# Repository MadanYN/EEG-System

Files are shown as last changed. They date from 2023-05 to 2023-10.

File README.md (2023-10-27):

# EEG-System
The aim of the project is to develop an ELectroencephalogram(EEG) Acquisition System that
is capable of monitoring brain activity through 24 different channels simultaneously. The system should convey the captured data in real-time to a computer over Bluetooth and the receiver should plot waveforms of all the channels. The design is inspired by the OpenBCI Cyton/Ganglion biosensing board, which is a well-known and widely used EEG system.

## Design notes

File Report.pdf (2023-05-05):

# EE344 - Electronic Design Lab OpenBCI based EEG Acquisition System Final Report

### Group 1 : TUE-29

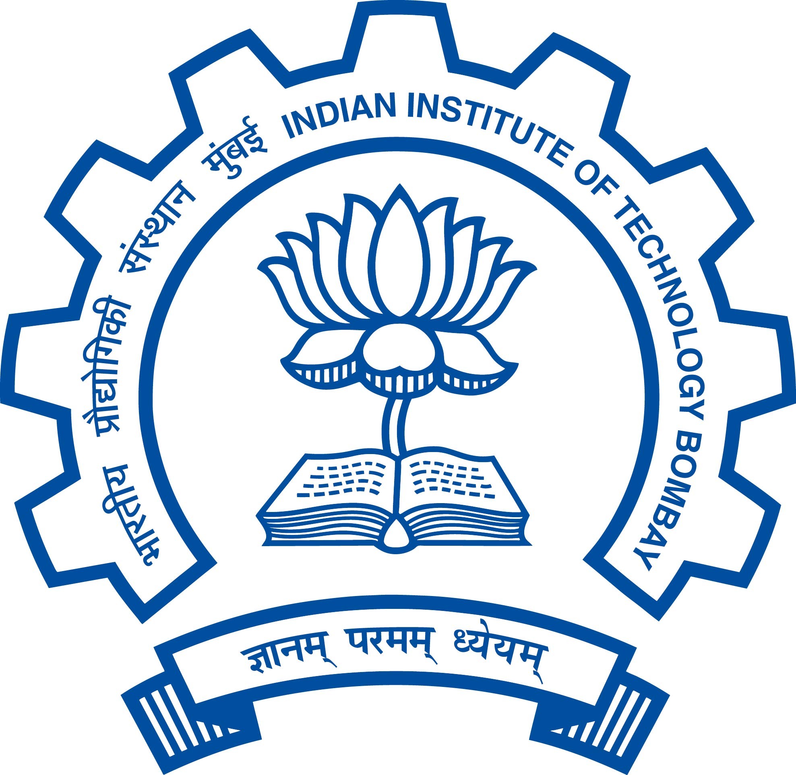
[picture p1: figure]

### Members : Madan Y N (200070040)

| Kushal Pawaskar (20D070059) Vaibhav Kumar (20D070087)
Group 2 : | MON-30

### Members : Gowtham S (20D070031)

| Saarthak Mittal (20D070066) Utkarsh Jindal (200070086)

### Guided by : Prof. Siddharth Tallur Prof. Laxmeesha Somappa

## Contents

1 Problem Statement | 3
2 Design | 3
2.1 | Block Diagram | | 3
2.2 | Design Schematic | | 5
2.3 | Bill of Materials | | 11
2.4 | CAD Models | | 12
3 Results and Observations | 13
3.1 | Data Acquisition | | 13
3.2 | Data Communication | | 14
4 Conclusions and Future Work | 17

## 1 Problem Statement

The aim of the project is to develop an ELectroencephalogram(EEG) Acquisition System that is capable of monitoring brain activity through 24 different channels simultaneously. The system should convey the captured data in real-time to a computer over Bluetooth and the receiver should plot waveforms of all the channels. The design is inspired by the OpenBCI Cy-ton/Ganglion biosensing board, which is a well-known and widely used EEG system.

## 2 Design

### 2.1 Block Diagram

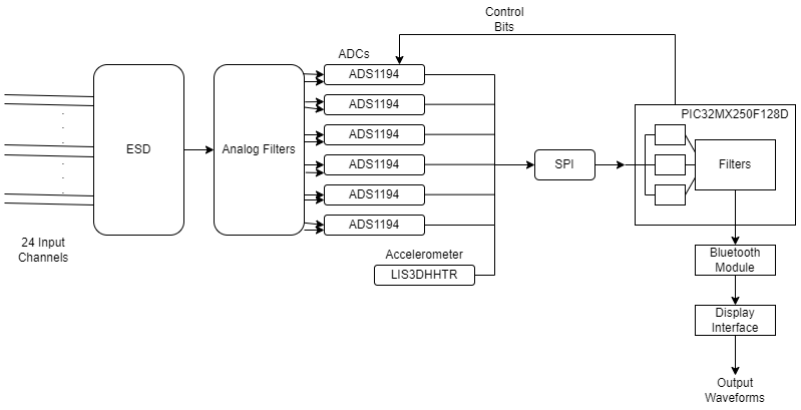
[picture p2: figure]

Explanation

The whole flowgraph can be divided into two broad sections which are namely data acquisition and data communication. The data acquisition consists of input channels which are 24 in number, ESD protection, low-pass filters to filter high frequency noise (EEG signals are typically in the range of few tens of hertz), ADS1194 which is a 16 bit ADC and LIS3DHHTR, an accelerometer to track head movements. Data communication consists of HC-05 bluetooth module to serially communicate data and a receiver end software to receive and plot waveforms in real-time.

Principle of Operation

The entire circuit can be classified into two subsystems based on two primary functions: data acquisition and processing, and data transmission. The principle of operation of each subsystem is as below.

- Data Acquisition

The data acquisition subsystem of our circuit consists of six ADS1194 Analog-to-Digital Converters, LIS3DHHT R Accelerometer and SD Card port. All these ICs are connected to SP I0 module of the microcontroller and are operated through time division multiple access.

Setup
This is the first stage in the operation of our circuit. Initially we will boot the microcontroller with our firmware through the UART1 module. After boot up, communication interfaces SP I0, UART0 ports are initialized. Next up, we set the programmable gains of all the six ADCs to 12 (the maximum allowed gain).

Update Channel Data
Default mode is the normal mode of operation. The chip select lines of the all the six ADCs are sequentially drawn low one at a time and a packet of data corresponding to one channel is received from each ADC. This way data is received from all the 24 channels in sequence; the raw data is processed and stored in an array.

Update Accelerometer Data
Similar to the previous stage, in this stage the chip select line corresponding to the accelerometer is drawn low. Data is read, processed and stored in an array.

Processing
In this stage input characters is received from PC through UART1 and according to the input the operation of the device is decided. The mode of operation of the board, from how many and from which all channels is the data needed to be collected, and many other control related decisions can be made in this stage.
- Data Transmission

HC-05 BLuetooth Classic Module
HC-05 provides fast and reliable data transmission. It has on-board 3.3 V voltage regulator so it can work with 5V as well.We are going to use UART between PIC µC and HC-05. It has few important pins as follows:
1. Enable: this pin is used to toggle between data and command mode.
2. Vcc : +5V power supply
3. Ground : 0V connection
4. Tx : transmits serial data, everything received via Bluetooth will be given out by this pin as serial data.
5. Rx : receives serial data, serial data given to this pin will be broadcasted via bluetooth.

Packet Format
Each packet contains a header byte, 24 channel data and accelerometer data, and a footer byte. The description is as follows:
Byte Range | Data Contained
1 | start byte
2-3 | channel 1 data
48-49 | channel 24 data
50-51 | accelerometer X data
52-53 | accelerometer Y data
54-55 | accelerometer Z data
56 | stop byte

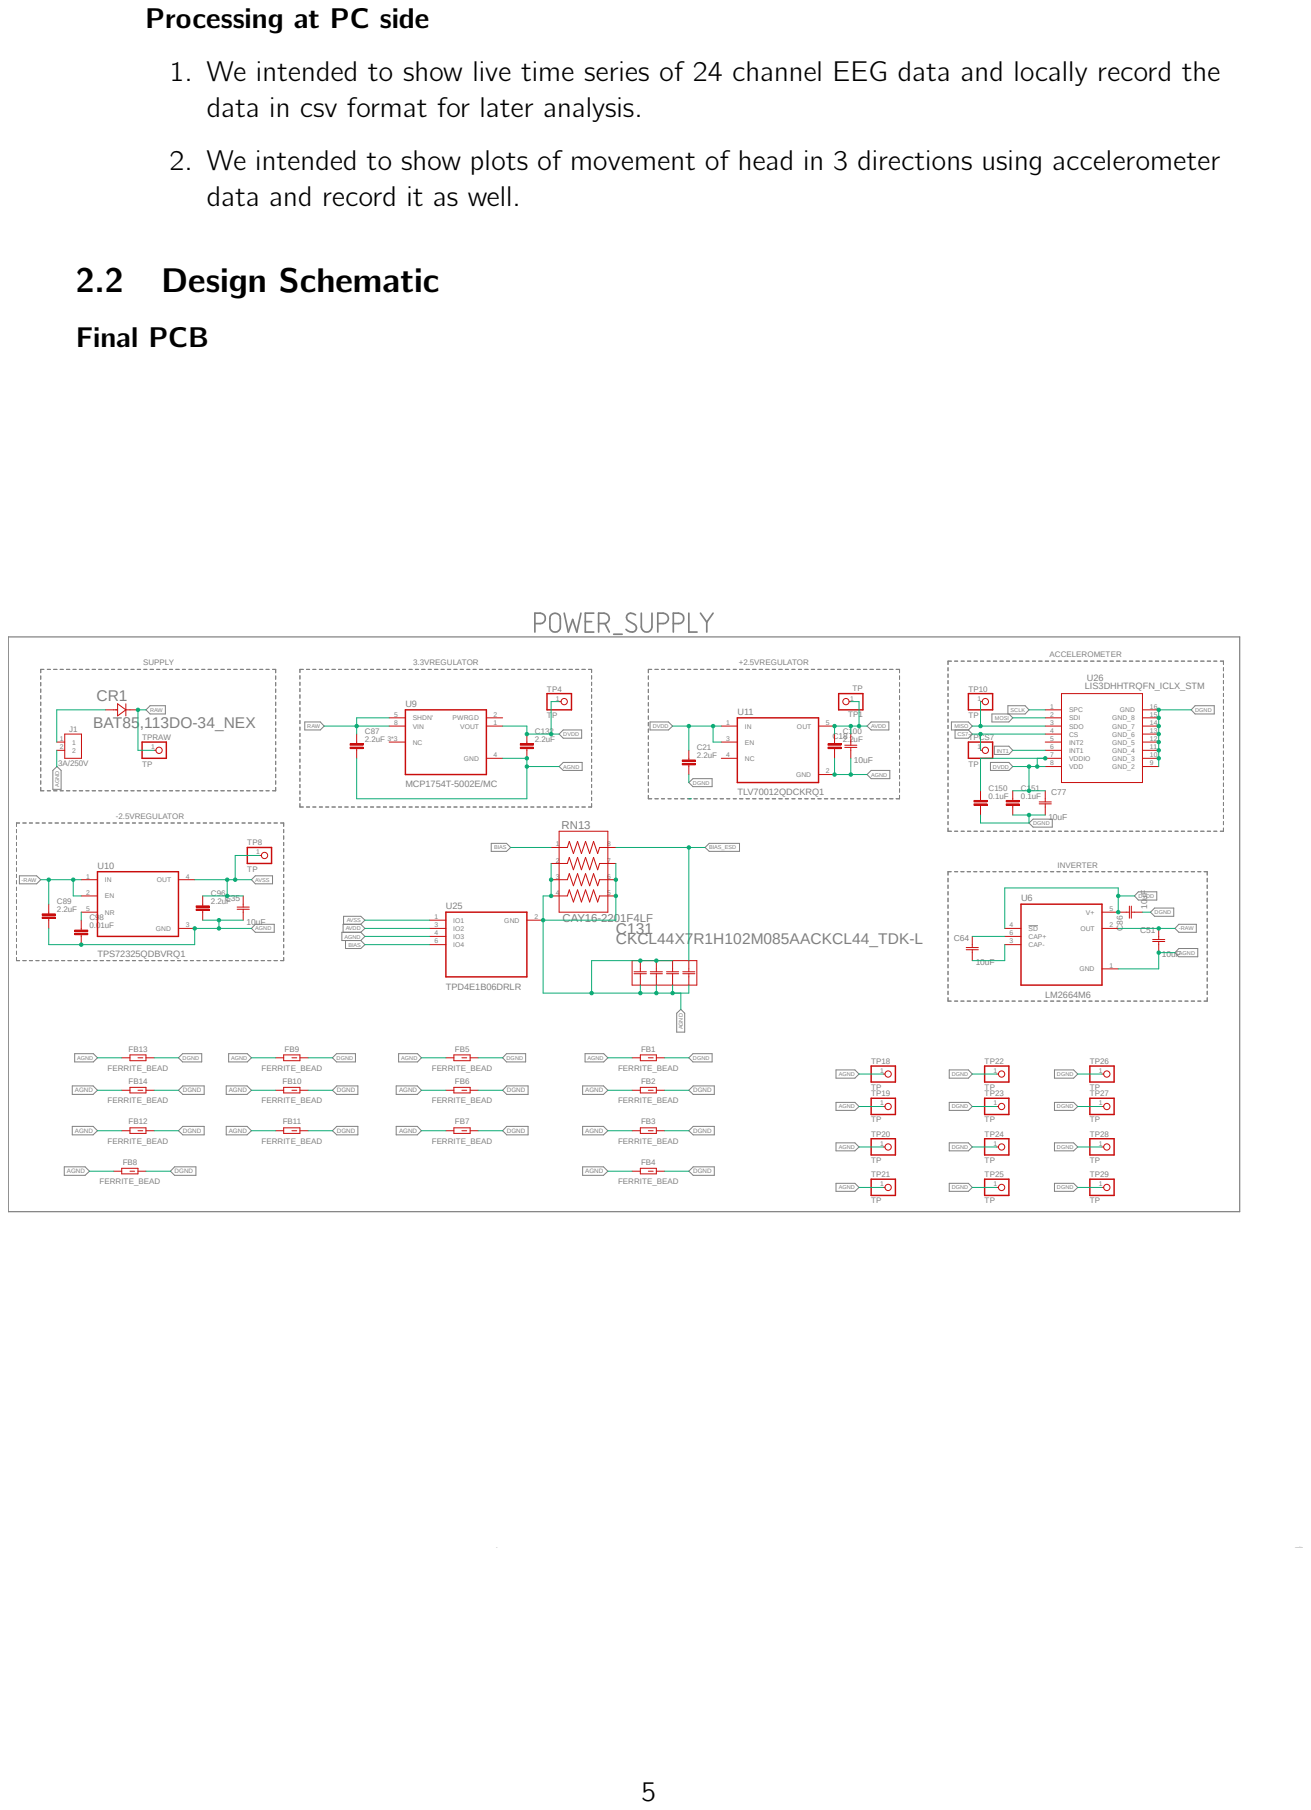
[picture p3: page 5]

Processing at PC side

1. We intended to show live time series of 24 channel EEG data and locally record the
data in csv format for later analysis.

2. We intended to show plots of movement of head in 3 directions using accelerometer
data and record it as well.

26-03-2023 12:26 f=0.56 C:\Users\hp\AppData\Local\Temp\Neutron\ElectronFileOutput\26880\sch-27726040-4bae-4901-84db-4ab1c912bd3d\BCI_MON_30_TUES_29 v1 v1.sch (Sheet: 1/1)

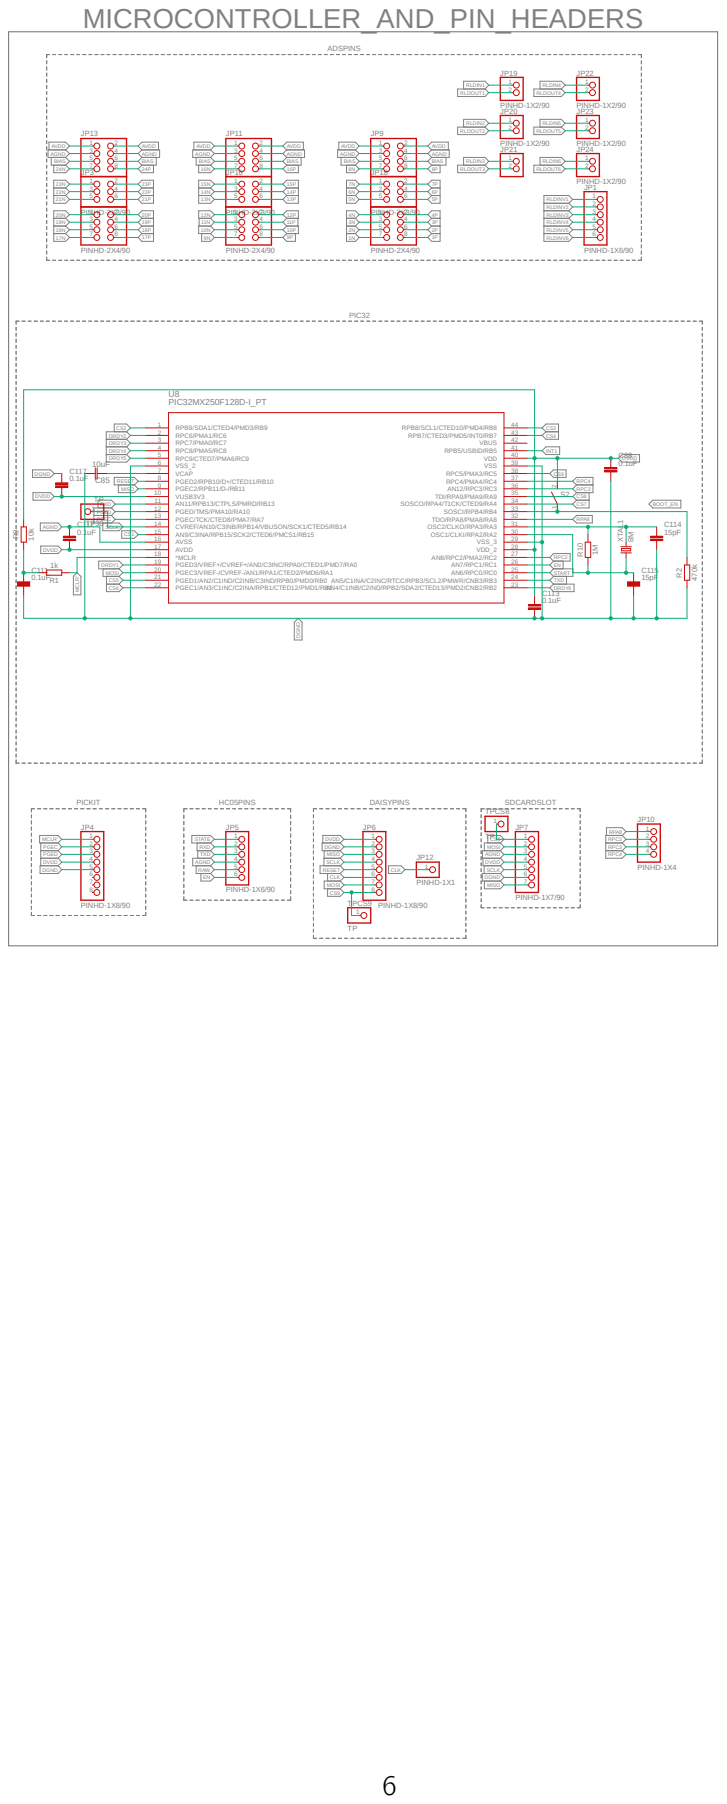
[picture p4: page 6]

# CAY16-2201F4LF ¹uF 0.1uF 1uF 0.1uF

IN8P 2 | RLDIN 62 | RLDINV 61 | RLDREF 60 | SCLK 40 | START 38 | VREFN 25 | VREFP 24 | GPIO1 42 | GPIO2 44 | RESV1 31 | VCAP1 28 | VCAP2 30 | VCAP3 55

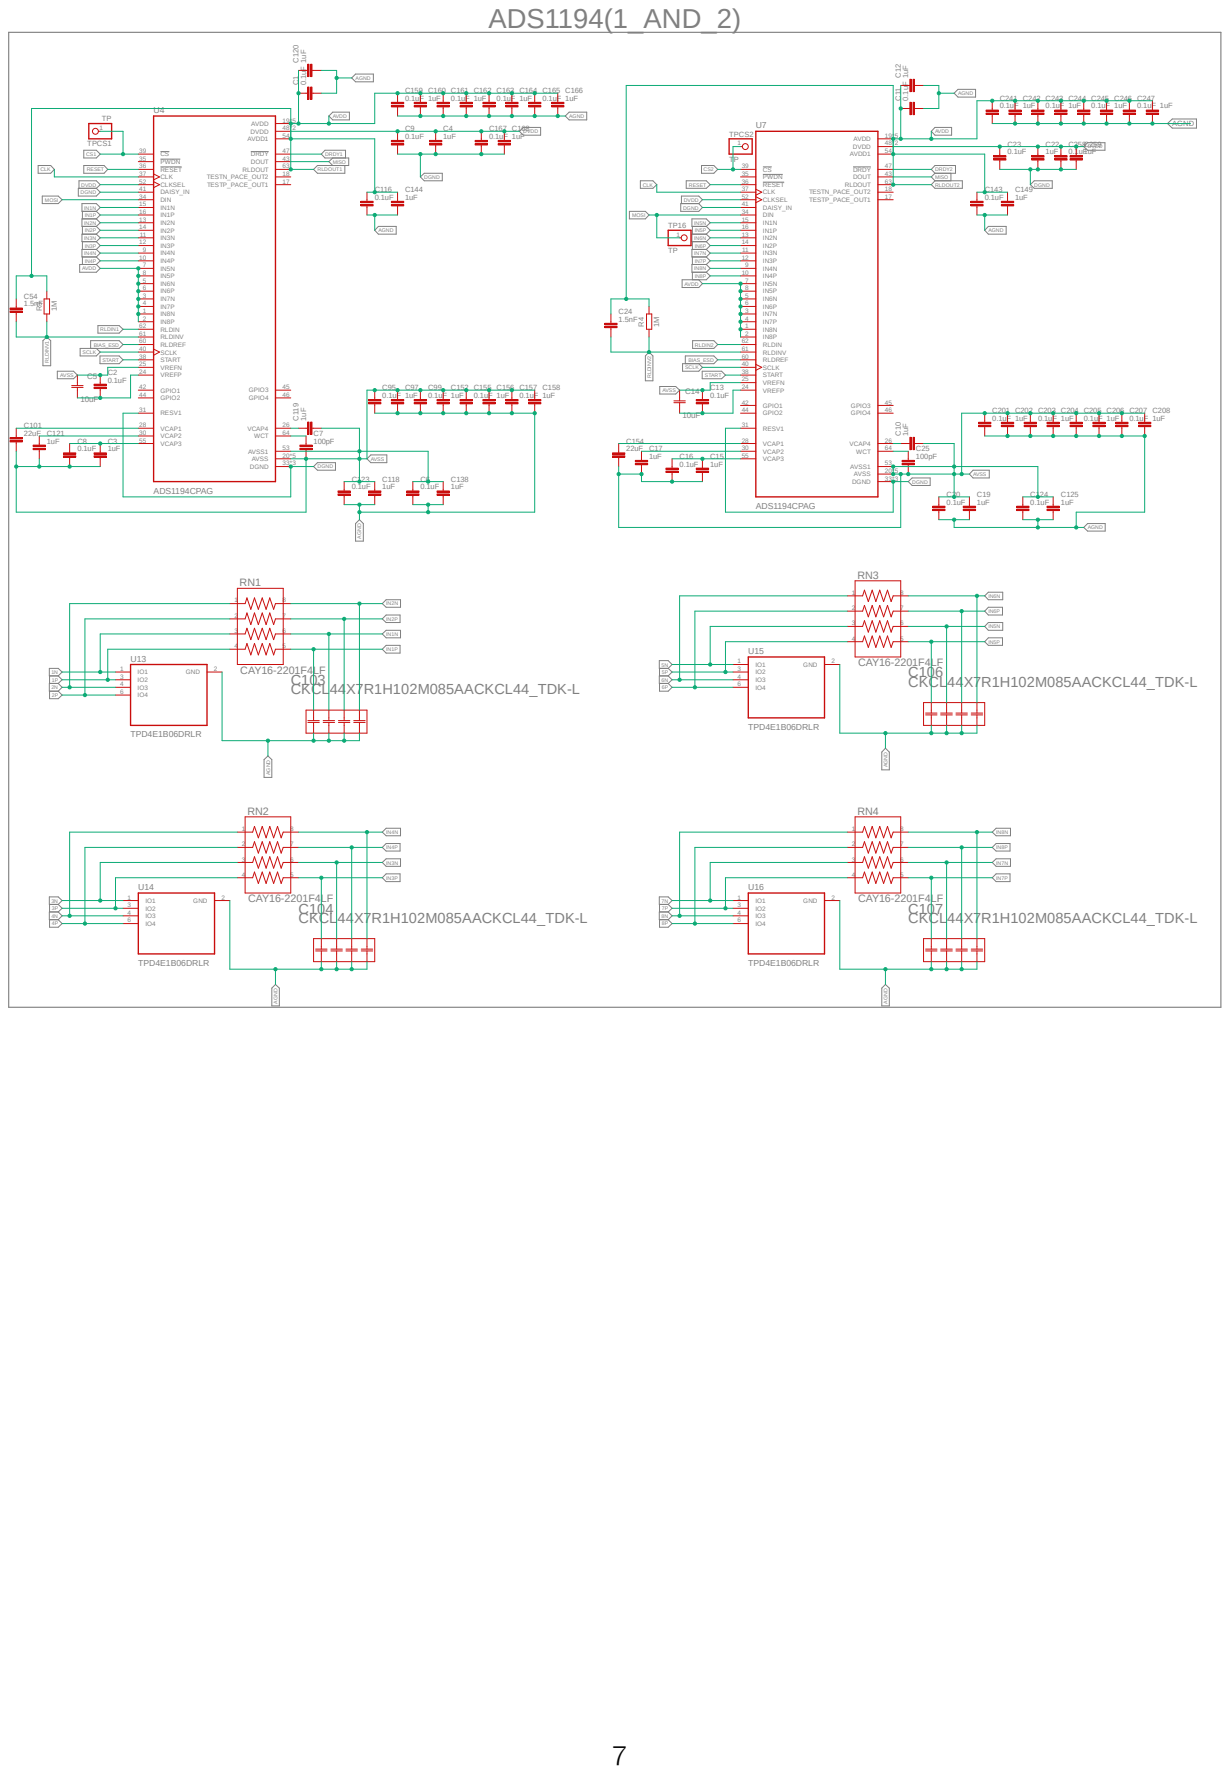
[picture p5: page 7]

ADS1194CPAG | 1uF 0.1uF 1uF 0.1uF
IN8P 2 | RLDIN 62 | RLDINV 61 | RLDREF 60 | SCLK 40 | START 38 | VREFN 25 | VREFP 24 | GPIO1 42 | GPIO2 44 | RESV1 31 | VCAP1 28 | VCAP2 30 | VCAP3 55

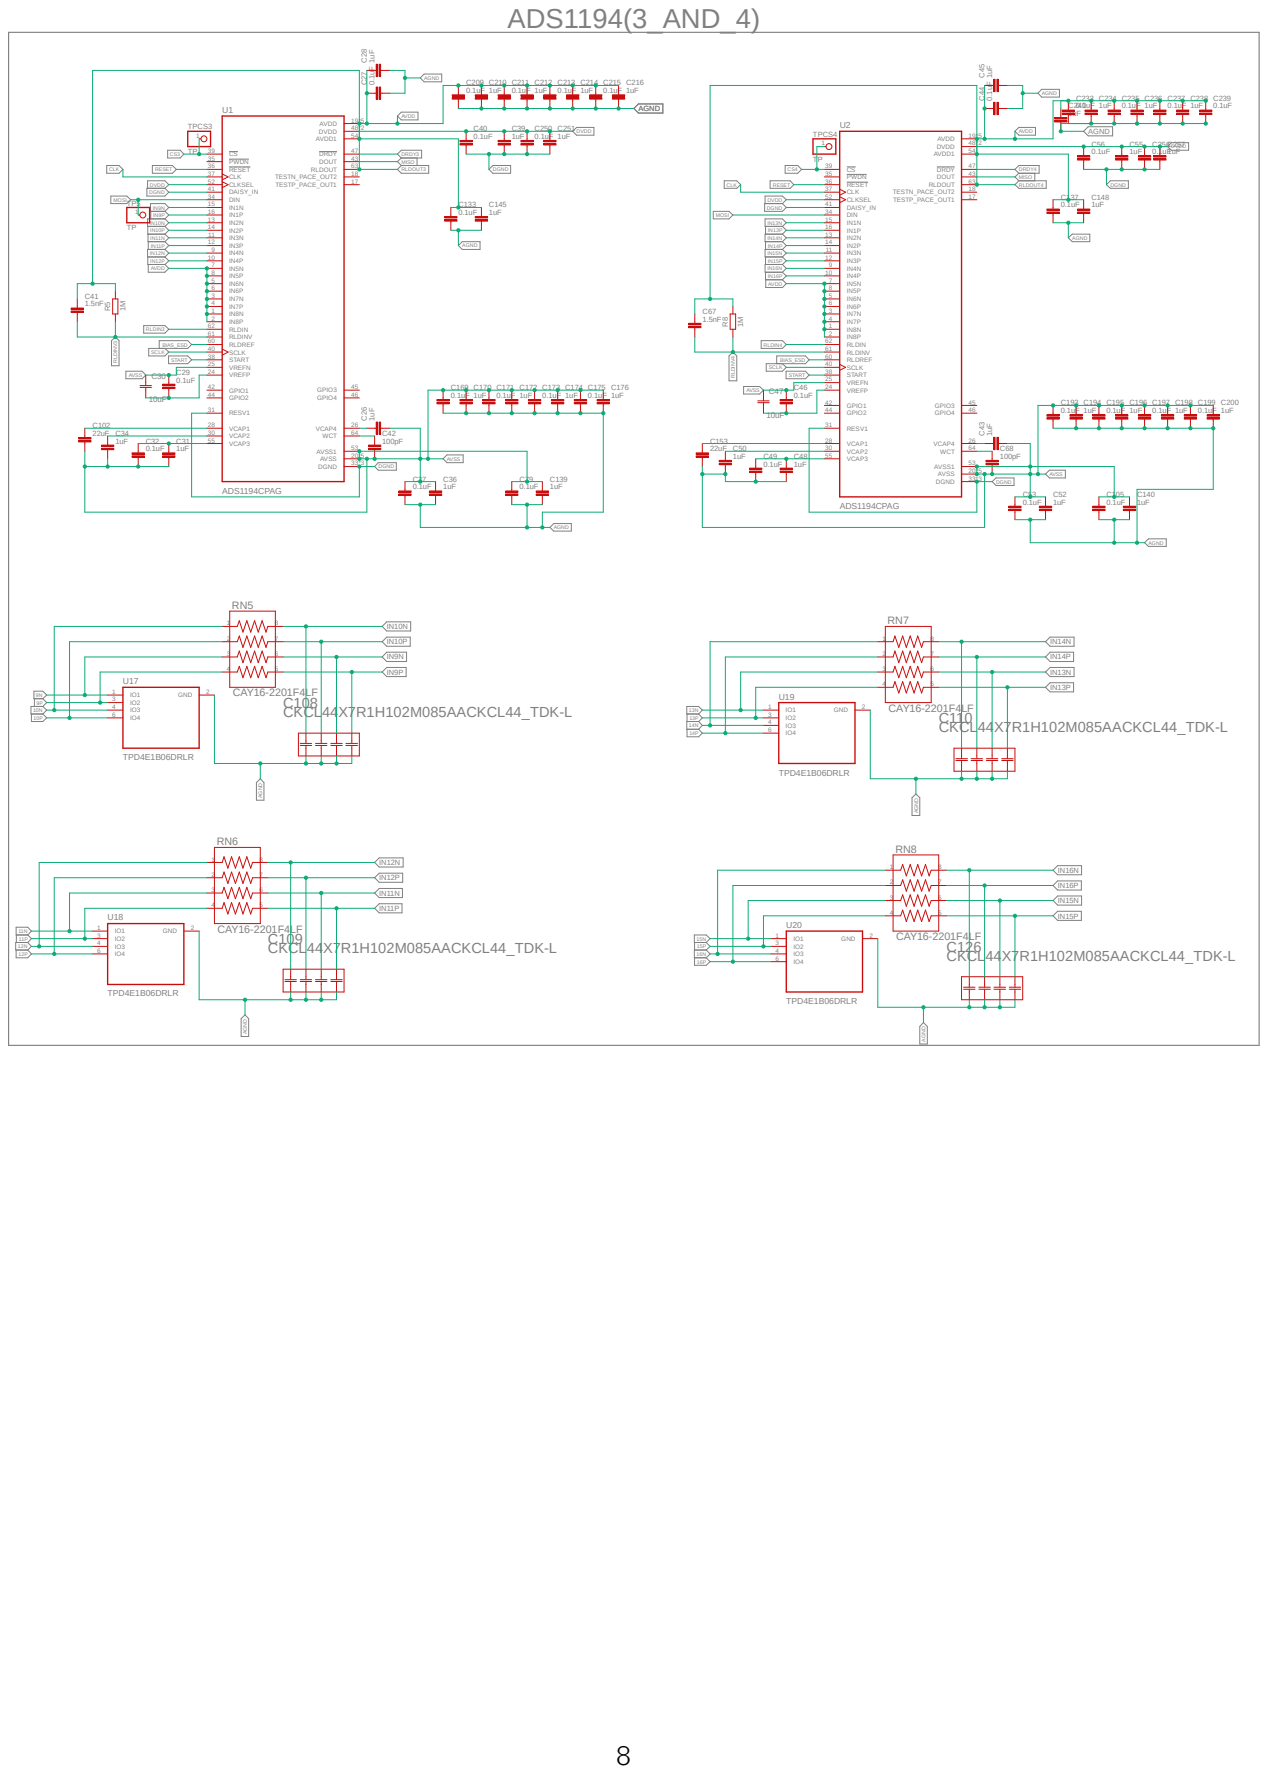
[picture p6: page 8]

IO2 3 | CAY16-2201F4LF CKCL44X7R1H102M085AACKCL44_TDK-L TPD4E1B06DRLR

ADS1194CPAG | 1uF 0.1uF 1uF
IN8P 2 | RLDIN 62 | RLDINV 61 | RLDREF 60 | SCLK 40 | START 38 | VREFN 25 | VREFP 24 | GPIO1 42 | GPIO2 44 | RESV1 31 | VCAP1 28 | VCAP2 30 | VCAP3 55

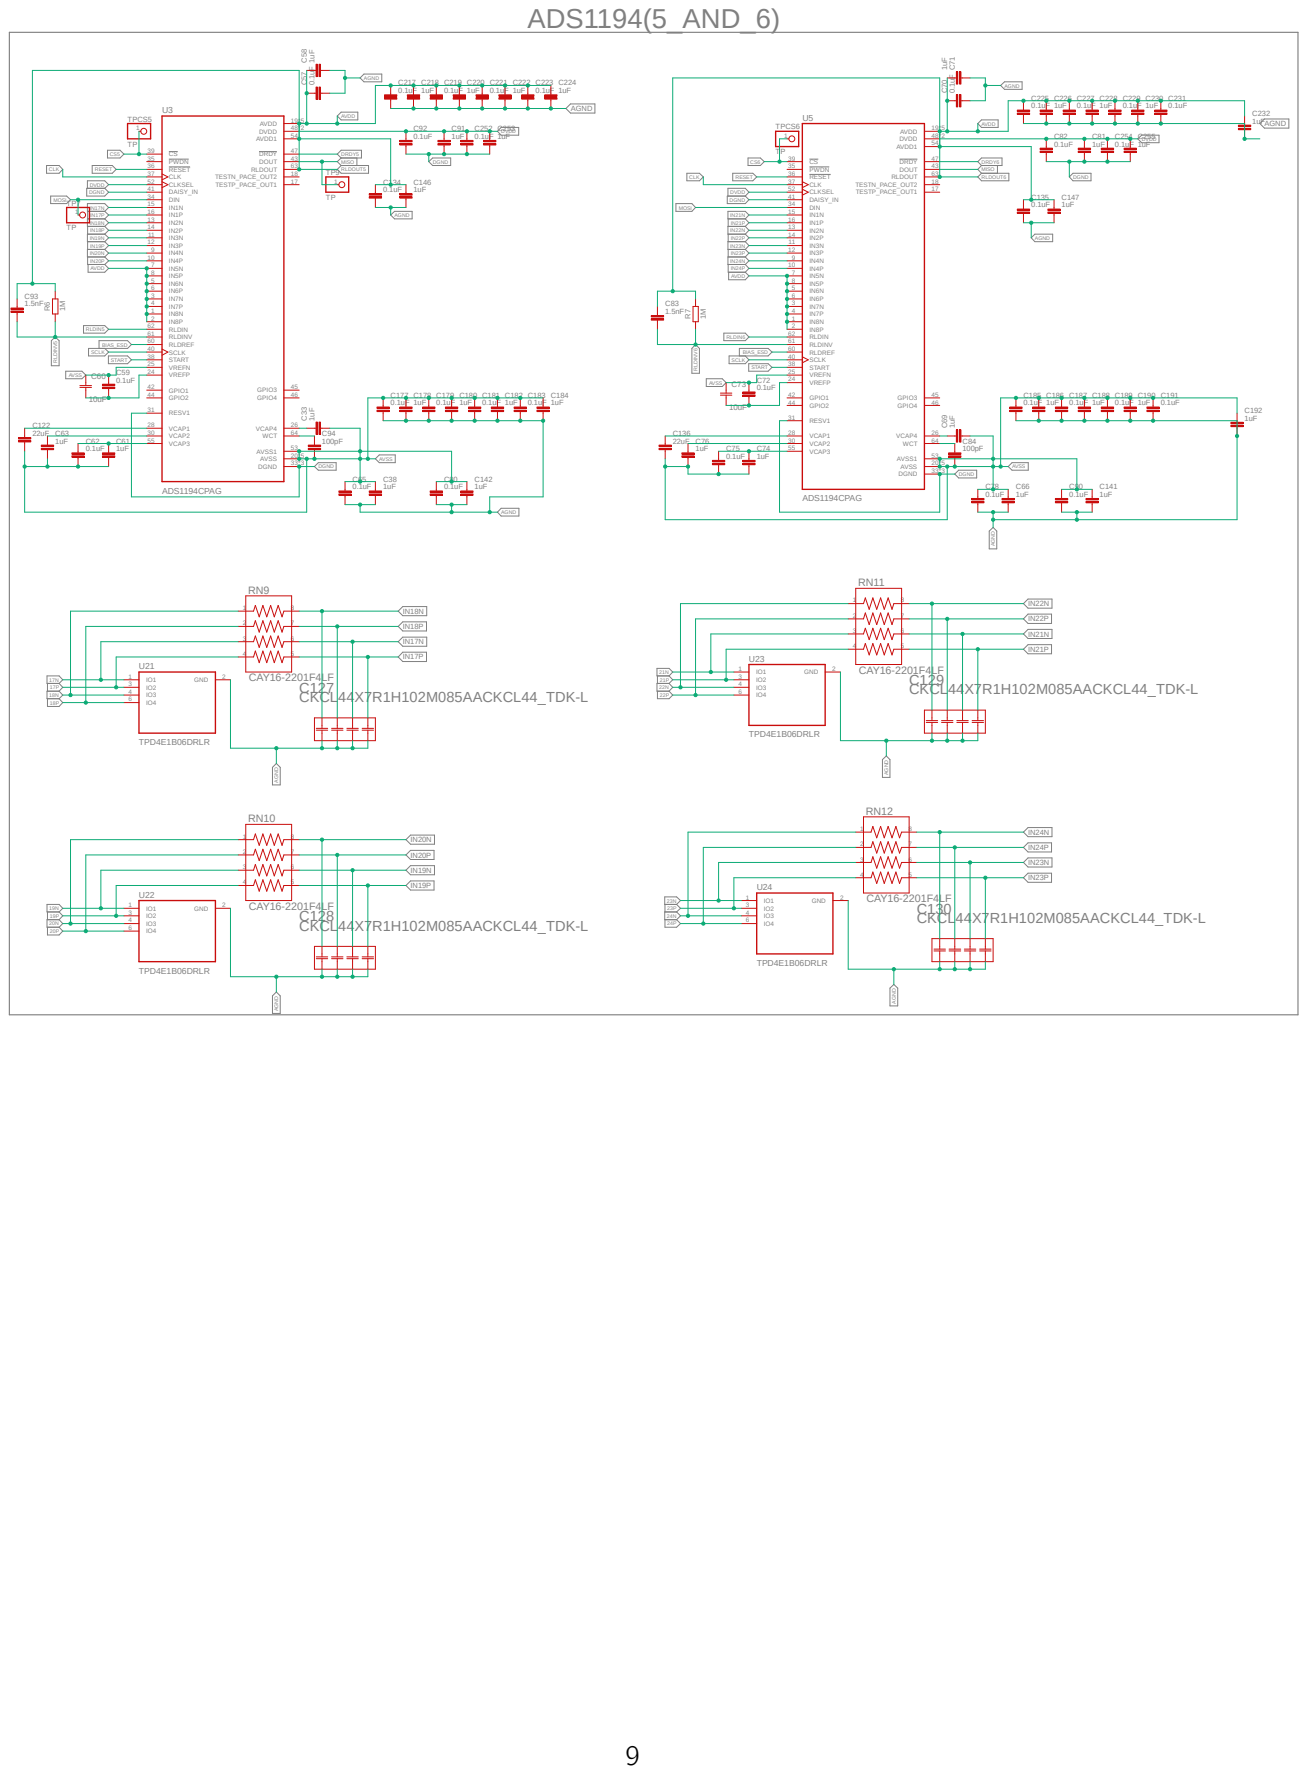
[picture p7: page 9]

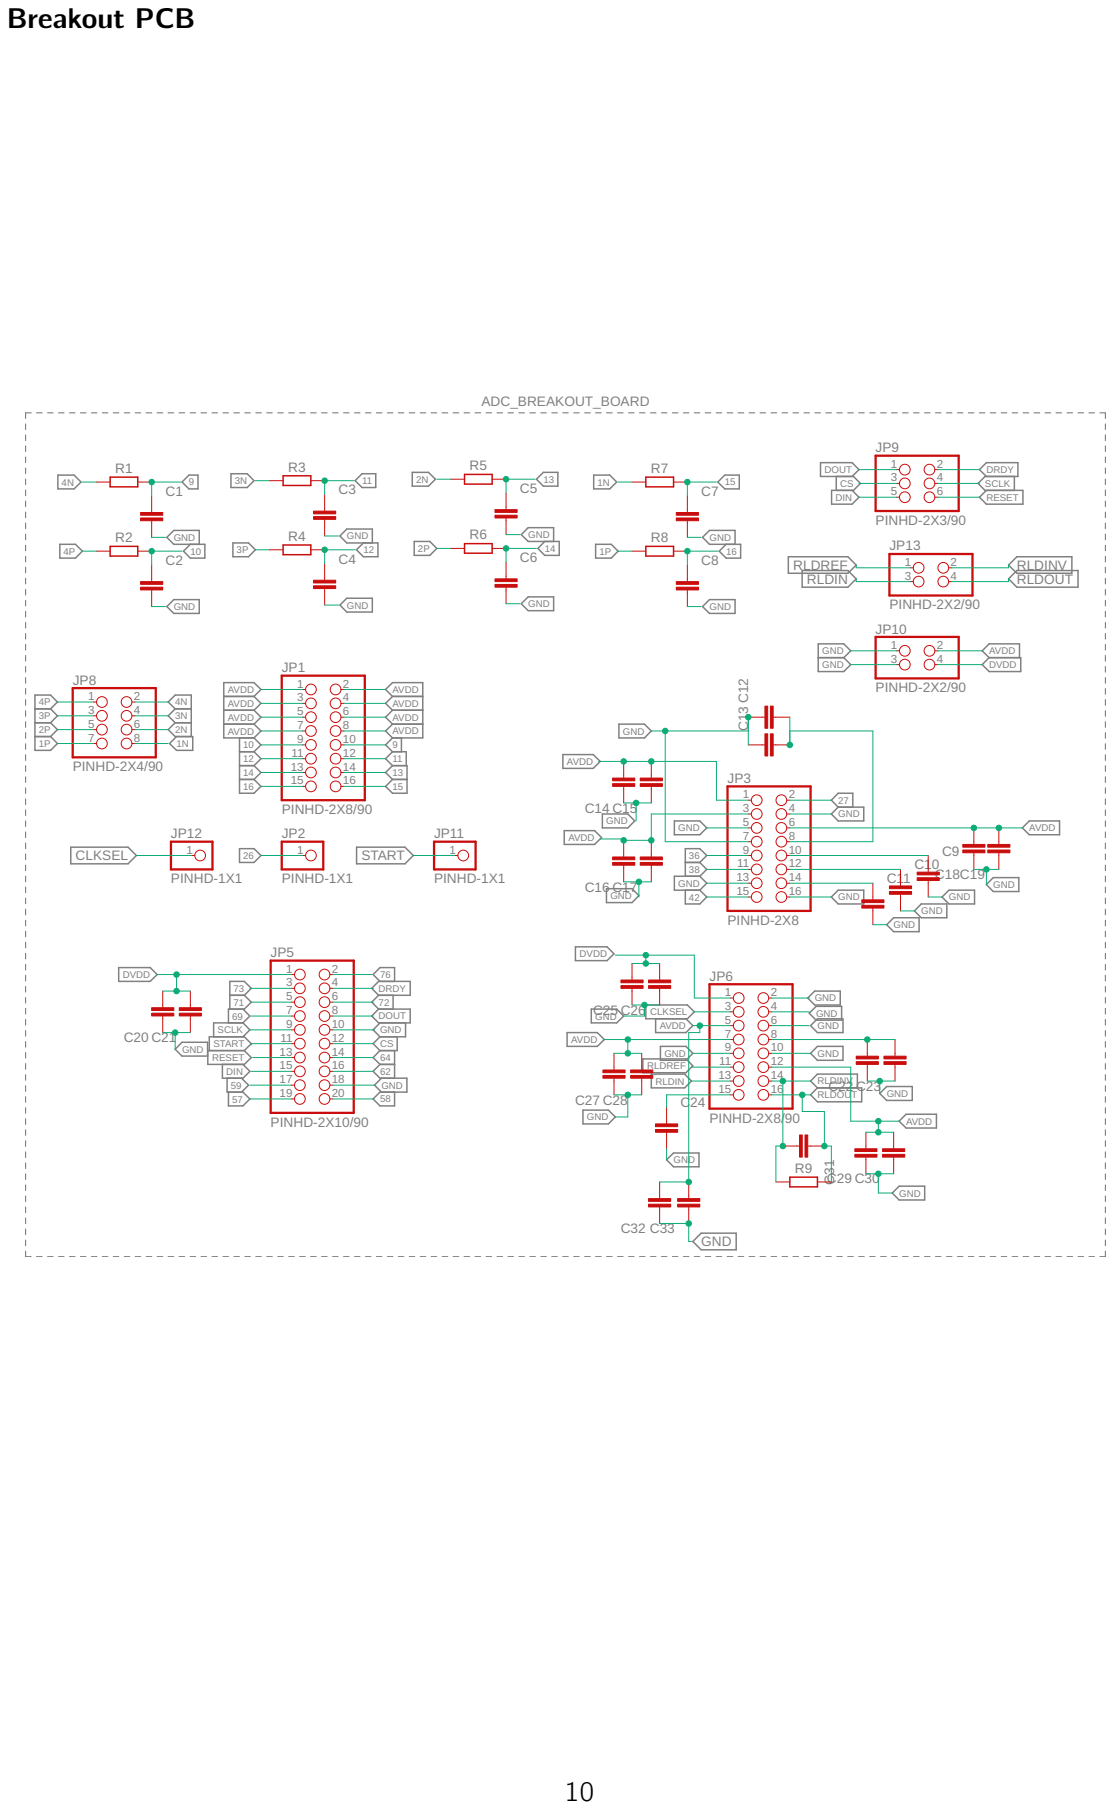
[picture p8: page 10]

RLDREF | 1 2 | RLDINV
RLDIN | 3 4 | RLDOUT

AVDD | | 7 8

11 12 | C10
13 14 | C11

### 2.3 Bill of Materials

Item Description | Component | Rate(in Rs.) | Quantity | Amount(in Rs.)
ADC | ADS1194 | 1135.53 | 6 | 6813.18
Microcontroller | PIC32MX250F128D | 463.17 | 1 | 463.17
Accelerometer | LIS3DHHTR | 1000 | 1 | 1000
Transient Voltage Suppressor | TPD4E1B06DRLR | 35.82 | 20 | 716.4
Voltage Regulator(+3V ) | MCP1754T-5002E/MC | 66.75 | 2 | 133.5
Voltage Regulator (−2.5V ) | TPS72325QDBVRQ1 | 301.99 | 1 | 301.99
Voltage Regulator (+2.5V ) | TLV70012QDCKRQ1 | 64.31 | 1 | 64.31
Voltage Inverter | LM2664M6X/NOPB | 74.89 | 1 | 74.89
0.1µF Capacitor | 04023C104KAT2A-62 | 30.12 | 18 | 542.16
1µF Capacitor | C1206C105K3NACAUTO | 43.14 | 16 | 690.24
10 µF Capacitor | C2012X7S1E106K125AE | 56.17 | 6 | 337.02
18 pF Capacitor | CBR04C180J5GACAUTO | 17.09 | 4 | 68.36
1 MΩ Resistor | RN73H2BTTD1004B25 | 58.61 | 2 | 117.22
470 kΩ Resistor | RN73H2ATTD4703B25 | 86.28 | 3 | 258.84
1KΩ Resistor | RN73H2BTTD1001B10 | 90.35 | 2 | 180.7
Capacitor Array | CKCL44X7R1H102M085AA | 29.30 | 17 | 498.1
2.2kΩ Resistor Array | CAY16-2201F4LF | 8.29 | 17 | 140.93

Total Amount : Rs. 13,726.55

### 2.4 CAD Models

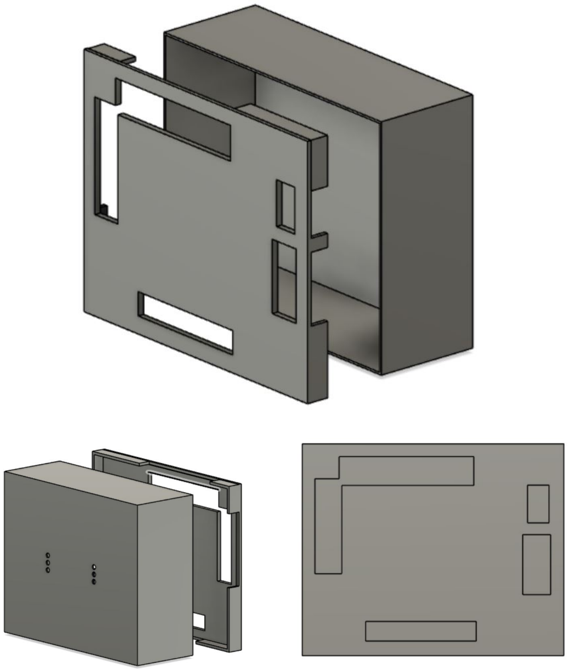
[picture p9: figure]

## 3 Results and Observations

### 3.1 Data Acquisition

Data acquisition from ADC has two parts: firstly, interfacing the ADC with microcontroller and reading the default register settings of the ADC and secondly, giving analog input signals to the input lines of the ADC and obtaining the converted digital values. It should be noted second part cannot proceed without completing the first part. We did four iterations of the first part and they are as follows,

- Iteration 1 — Breadboard circuit of ADC with Arduino development board

– AVDD - 5V from external source

– DVDD - 3.3V from external source

The setup and the ADC supply connections made are given in the below images

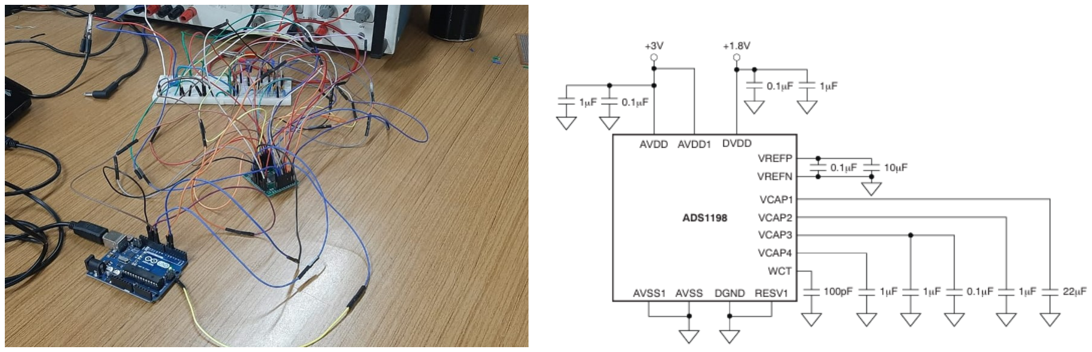
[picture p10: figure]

Figure 1: Setup (left) and ADC supply connections(right)

Result: The ADC gave 0x00 as reading of all the registers which implies that the ADC power-on hasn’t been done properly.

Possible Reason: Arduino development board has a logic high level of 5V but the ADC has digital high of 3.3V and this might have damaged the IC and consequently resulted in failure of the test.

- Iteration 2 — Breakout PCB with PIC32MX clicker board

– AVDD - 5V from clicker board

– DVDD - 3.3V from clicker board

The ADC supply connections made are same as those of iteration 1. The digital high of the clicker board is 3.3V which matches with logic high of the ADC.

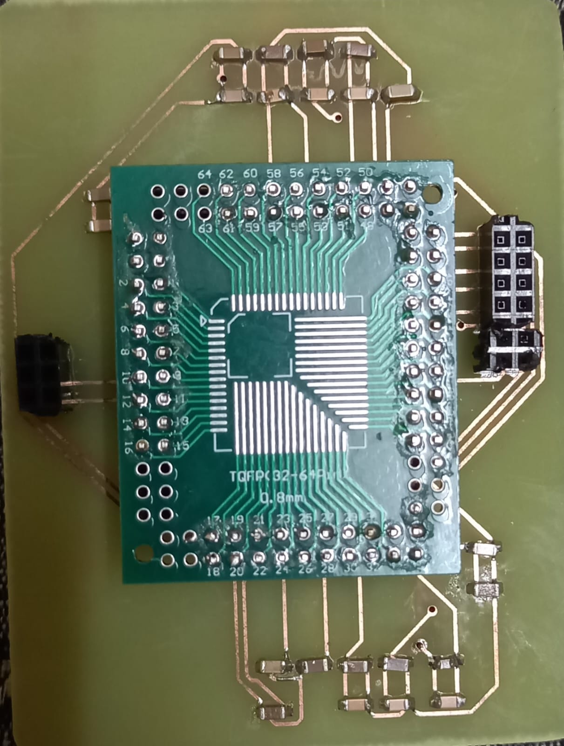
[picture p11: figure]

Figure 2: Breakout PCB with ADC setup

Result: The ADC gave 0x00 as reading of all the registers which implies that the ADC power-on hasn’t been done properly.

Reason: Error was found in some of the decoupling capacitor connections which caused the effective voltage at the pin lower than the required voltage.

- Iteration 3 — Breadboard circuit of ADC with clicker development board

– AVDD - 5V from clicker board

– DVDD - 3.3V from clicker board

The ADC supply connections made are same as those of iteration 1 & 2. The digital high of the clicker board is 3.3V which matches with logic high of the ADC.

Result: The ADC gave 0x00 as reading of all the registers which implies that the ADC power-on hasn’t been done properly.

Possible Reason: In this iteration of the testing, we used the same ADC chip that was used in iteration 2, which may have been damaged while doing iteration 2 .

- Iteration 4 — New breakout PCB board The mistakes in the previous iteration on breakout pcb were rectified and a new breakout PCB was designed.

Result: The testing could not be done since PCB could not be printed in time for the submission.

Reason: It was too late when we got to know that PCBLab was under maintenance and outside vendors could not deliver the PCB in time.

### 3.2 Data Communication

The objective is to transmit 24-channel data (16-bit each) from µC to PC. We used bluetooth for transmitting data thorough UART. We used HC05 bluetooth module for this purpose. The main tasks in data communication are transmitting data to PC using HC05, plotting real-time channel data, and storing locally in csv file for any other purpose.

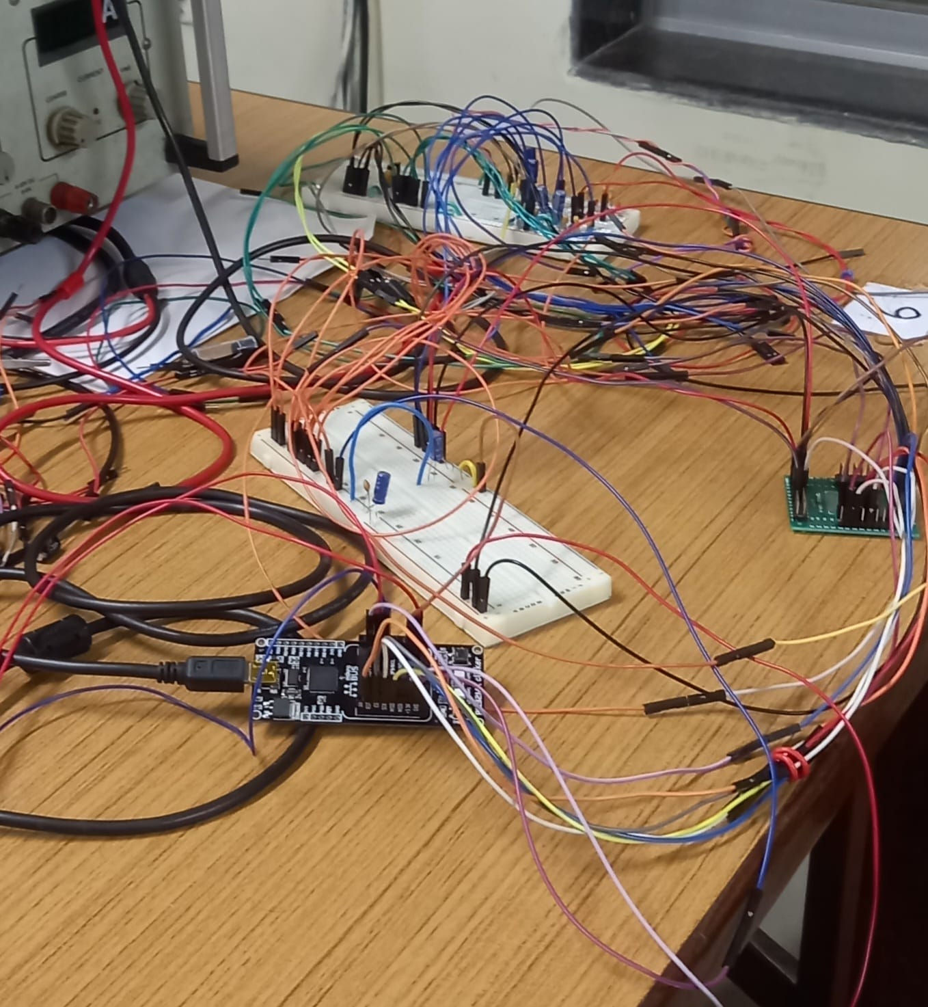
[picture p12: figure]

Figure 3: Breadboard circuit setup for ADC testing using clicker board

Block diagrams

- Data transmission at microcontroller : Since we were not able to finish ADC part so here we generate uniformly random 24 channels data (16 bit each) for transmission. We used UART for serial connection. We have added a delay in data generation to simulate the behaviour of ADC because it digitise input upto a fixed rate.The block diagram for code

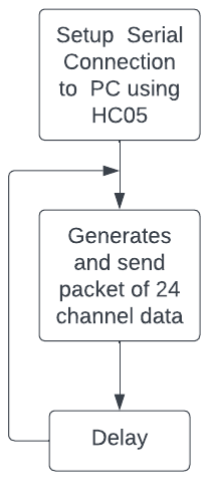
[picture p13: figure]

- Data reception at PC: We used PySerial Python module for serial connection to HC05.We run a python script on PC which continuously looks for packet header and then collects 24 channel data ,write all channels data to csv file. 16 bit channel data is appropriately converted to (typical) range (−100µV to 100µV ) using gain factor as per ADC resolution.

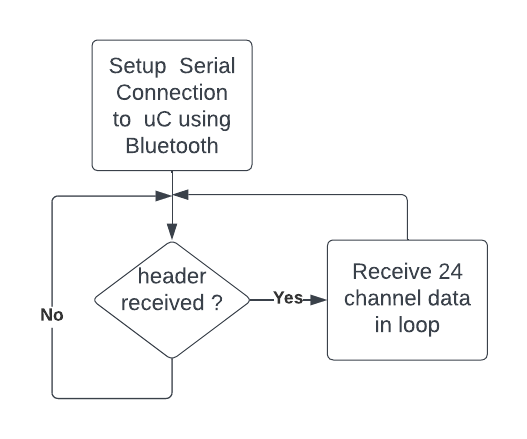
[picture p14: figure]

We did two iteration for bluetooth and the results are as follows :

- Iteration 1: We used arduino to send the channel data through UART using HC05 and used python to receive channel data as described in block diagram.

Result: We were able to successfully transmit and receive data through using bluetooth, we stored it locally in csv file but we were not able to plot the data in real time because data is received at fast rate (1 packet of 24 channel data every 50-60ms) and real time updation of plot is causing PC to froze. Hence, we stored the data and plotted it locally later after complete reception.

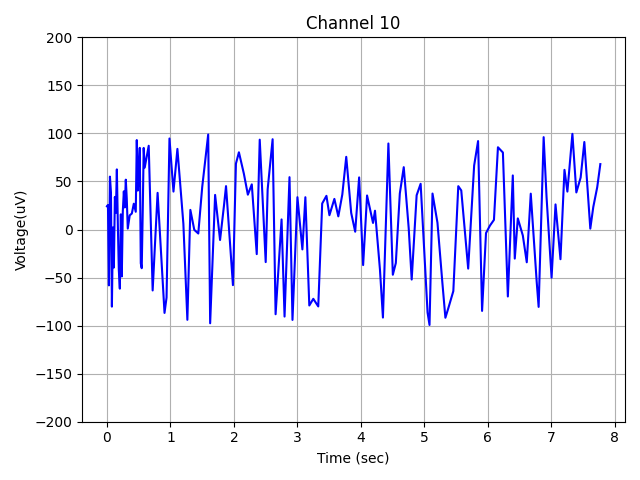
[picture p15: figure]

Video Demonstration :
https://drive.google.com/drive/folders/1LYR-3z1IbRmSmTMcULbhplSOKwMd8xXk?usp=sharing (https://drive.google.com/drive/folders/1LYR-3z1IbRmSmTMcULbhplSOKwMd8xXk?usp=sharing)
- Iteration 2: In this iteration, we did transmission of data with clicker (development) board since our pcb is not ready and ADC part is still not completed. The data receiving and plotting is same as iteration 1.

Result: This iteration was not fully successful. The data transmission from clicker board using uart with bluetooth was happening but the data received was not in correct encoding. We tried various different decoding format but couldn’t find the solution. We don’t know exact reason behind the problem but our guess is either encoding issue or pull up register issue.

## 4 Conclusions and Future Work

The aim of the project to build a 24-channel EEG acquisition system could not be achieved in the stipulated time. We completed a compact standalone PCB for the whole 24-channel system. We also demonstrated transceiving data over bluetooth. Future work would start with completing iteration 4 of the ADC testing and then move to channel data acquisition by a single ADC and finally by all the six ADCs as in the final design. One more improvement on the design may be, instead of designing a single PCB with all 24 channels, we can make a modular design which would allow customization of number of channels as 8 or 16 or 24.

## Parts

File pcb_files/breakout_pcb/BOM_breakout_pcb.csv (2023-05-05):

Part | Value | Device | Package | Description | CATEGORY | DESCRIPTION | MANUFACTURER | MPN | OPERATING_TEMP | PART_STATUS | RATING | ROHS_COMPLIANT | SERIES | SUB-CATEGORY | THERMALLOSS | TOLERANCE | TYPE | VOLTAGE_RATING
C1 |  | C_TANTALUM-1206(3216-METRIC) | CAPM3216X180 | Capacitor - Generic | Capacitor
C2 |  | C_TANTALUM-1206(3216-METRIC) | CAPM3216X180 | Capacitor - Generic | Capacitor
C3 |  | C_TANTALUM-1206(3216-METRIC) | CAPM3216X180 | Capacitor - Generic | Capacitor
C4 |  | C_TANTALUM-1206(3216-METRIC) | CAPM3216X180 | Capacitor - Generic | Capacitor
C5 |  | C_TANTALUM-1206(3216-METRIC) | CAPM3216X180 | Capacitor - Generic | Capacitor
C6 |  | C_TANTALUM-1206(3216-METRIC) | CAPM3216X180 | Capacitor - Generic | Capacitor
C7 |  | C_TANTALUM-1206(3216-METRIC) | CAPM3216X180 | Capacitor - Generic | Capacitor
C8 |  | C_TANTALUM-1206(3216-METRIC) | CAPM3216X180 | Capacitor - Generic | Capacitor
C9 |  | C_TANTALUM-1206(3216-METRIC) | CAPM3216X180 | Capacitor - Generic | Capacitor
C10 |  | C_TANTALUM-1206(3216-METRIC) | CAPM3216X180 | Capacitor - Generic | Capacitor
C11 |  | C_TANTALUM-1206(3216-METRIC) | CAPM3216X180 | Capacitor - Generic | Capacitor
C12 |  | C_TANTALUM-1206(3216-METRIC) | CAPM3216X180 | Capacitor - Generic | Capacitor
C13 |  | C_TANTALUM-1206(3216-METRIC) | CAPM3216X180 | Capacitor - Generic | Capacitor
C14 |  | C_TANTALUM-1206(3216-METRIC) | CAPM3216X180 | Capacitor - Generic | Capacitor
C15 |  | C_TANTALUM-1206(3216-METRIC) | CAPM3216X180 | Capacitor - Generic | Capacitor
C16 |  | C_TANTALUM-1206(3216-METRIC) | CAPM3216X180 | Capacitor - Generic | Capacitor
C17 |  | C_TANTALUM-1206(3216-METRIC) | CAPM3216X180 | Capacitor - Generic | Capacitor
C18 |  | C_TANTALUM-1206(3216-METRIC) | CAPM3216X180 | Capacitor - Generic | Capacitor
C19 |  | C_TANTALUM-1206(3216-METRIC) | CAPM3216X180 | Capacitor - Generic | Capacitor
C20 |  | C_TANTALUM-1206(3216-METRIC) | CAPM3216X180 | Capacitor - Generic | Capacitor
C21 |  | C_TANTALUM-1206(3216-METRIC) | CAPM3216X180 | Capacitor - Generic | Capacitor
C22 |  | C_TANTALUM-1206(3216-METRIC) | CAPM3216X180 | Capacitor - Generic | Capacitor
C23 |  | C_TANTALUM-1206(3216-METRIC) | CAPM3216X180 | Capacitor - Generic | Capacitor
C24 |  | C_TANTALUM-1206(3216-METRIC) | CAPM3216X180 | Capacitor - Generic | Capacitor
C25 |  | C_TANTALUM-1206(3216-METRIC) | CAPM3216X180 | Capacitor - Generic | Capacitor
C26 |  | C_TANTALUM-1206(3216-METRIC) | CAPM3216X180 | Capacitor - Generic | Capacitor
C27 |  | C_TANTALUM-1206(3216-METRIC) | CAPM3216X180 | Capacitor - Generic | Capacitor
C28 |  | C_TANTALUM-1206(3216-METRIC) | CAPM3216X180 | Capacitor - Generic | Capacitor
C29 |  | C_TANTALUM-1206(3216-METRIC) | CAPM3216X180 | Capacitor - Generic | Capacitor
C30 |  | C_TANTALUM-1206(3216-METRIC) | CAPM3216X180 | Capacitor - Generic | Capacitor
C31 |  | C_TANTALUM-1206(3216-METRIC) | CAPM3216X180 | Capacitor - Generic | Capacitor
C32 |  | C_TANTALUM-1206(3216-METRIC) | CAPM3216X180 | Capacitor - Generic | Capacitor
C33 |  | C_TANTALUM-1206(3216-METRIC) | CAPM3216X180 | Capacitor - Generic | Capacitor
JP1 | PINHD-2X8/90 | PINHD-2X8/90 | 2X08/90 | PIN HEADER | CONNECTOR |  |  |  |  |  |  |  |  | PIN-HEADER
JP2 | PINHD-1X1 | PINHD-1X1 | 1X01 | PIN HEADER | CONNECTOR |  |  |  |  |  |  |  |  | PIN-HEADER
JP3 | PINHD-2X8 | PINHD-2X8 | 2X08 | PIN HEADER | CONNECTOR |  |  |  |  |  |  |  |  | PIN-HEADER
JP5 | PINHD-2X10/90 | PINHD-2X10/90 | 2X10/90 | PIN HEADER | CONNECTOR |  |  |  |  |  |  |  |  | PIN-HEADER
JP6 | PINHD-2X8/90 | PINHD-2X8/90 | 2X08/90 | PIN HEADER | CONNECTOR |  |  |  |  |  |  |  |  | PIN-HEADER
JP8 | PINHD-2X4/90 | PINHD-2X4/90 | 2X04/90 | PIN HEADER | CONNECTOR |  |  |  |  |  |  |  |  | PIN-HEADER
JP9 | PINHD-2X3/90 | PINHD-2X3/90 | 2X03/90 | PIN HEADER | CONNECTOR |  |  |  |  |  |  |  |  | PIN-HEADER
JP10 | PINHD-2X2/90 | PINHD-2X2/90 | 2X02/90 | PIN HEADER | CONNECTOR |  |  |  |  |  |  |  |  | PIN-HEADER
JP11 | PINHD-1X1 | PINHD-1X1 | 1X01 | PIN HEADER | CONNECTOR |  |  |  |  |  |  |  |  | PIN-HEADER
JP12 | PINHD-1X1 | PINHD-1X1 | 1X01 | PIN HEADER | CONNECTOR |  |  |  |  |  |  |  |  | PIN-HEADER
JP13 | PINHD-2X2/90 | PINHD-2X2/90 | 2X02/90 | PIN HEADER | CONNECTOR |  |  |  |  |  |  |  |  | PIN-HEADER
R1 |  | R_CHIP-1206(3216-METRIC) | RESC3216X70 | Resistor Fixed - Generic | Resistor |  |  |  |  |  |  |  |  | Fixed
R2 |  | R_CHIP-1206(3216-METRIC) | RESC3216X70 | Resistor Fixed - Generic | Resistor |  |  |  |  |  |  |  |  | Fixed
R3 |  | R_CHIP-1206(3216-METRIC) | RESC3216X70 | Resistor Fixed - Generic | Resistor |  |  |  |  |  |  |  |  | Fixed
R4 |  | R_CHIP-1206(3216-METRIC) | RESC3216X70 | Resistor Fixed - Generic | Resistor |  |  |  |  |  |  |  |  | Fixed
R5 |  | R_CHIP-1206(3216-METRIC) | RESC3216X70 | Resistor Fixed - Generic | Resistor |  |  |  |  |  |  |  |  | Fixed
R6 |  | R_CHIP-1206(3216-METRIC) | RESC3216X70 | Resistor Fixed - Generic | Resistor |  |  |  |  |  |  |  |  | Fixed
R7 |  | R_CHIP-1206(3216-METRIC) | RESC3216X70 | Resistor Fixed - Generic | Resistor |  |  |  |  |  |  |  |  | Fixed
R8 |  | R_CHIP-1206(3216-METRIC) | RESC3216X70 | Resistor Fixed - Generic | Resistor |  |  |  |  |  |  |  |  | Fixed
R9 |  | R_CHIP-1206(3216-METRIC) | RESC3216X70 | Resistor Fixed - Generic | Resistor |  |  |  |  |  |  |  |  | Fixed

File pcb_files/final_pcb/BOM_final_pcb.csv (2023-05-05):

Part | Value | Device | Package | Description | CATEGORY | COPYRIGHT | DESCRIPTION | FILTER_TYPE | FREQUENCY | IMPEDANCE_FREQ | MANUFACTURER | MANUFACTURER_PART_NUMBER | MFR_NAME | MPN | OPERATING_TEMP | OPERATING_TEMPERATURE | PACKAGE | PART_STATUS | RATING | REVERSE_VOLTAGE | ROHS_COMPLIANCE | ROHS_COMPLIANT | SERIES | STANDARD | SUB-CATEGORY | SUBCATEGORY | SUB_CATEGORY | THERMALLOSS | THERMAL_LOSS | TOLERANCE | TYPE | VALUE | VOLTAGE_RATING
C1 | 0.1uF | C_CHIP-0805(2012-METRIC) | CAPC2012X110 | Capacitor - Generic | Capacitor
C2 | 0.1uF | C_CHIP-0805(2012-METRIC) | CAPC2012X110 | Capacitor - Generic | Capacitor
C3 | 1uF | C_CHIP-0805(2012-METRIC) | CAPC2012X110 | Capacitor - Generic | Capacitor
C4 | 1uF | C_CHIP-0805(2012-METRIC) | CAPC2012X110 | Capacitor - Generic | Capacitor
C5 | 10uF | 293D106X0016A2TE3CAP_293D-A_VSS | CAP_293D-A_VSS |  |  | Copyright (C) 2023 Ultra Librarian. All rights reserved. |  |  |  |  |  | 293D106X0016A2TE3 | Vishay
C6 | 0.1uF | C_CHIP-0805(2012-METRIC) | CAPC2012X110 | Capacitor - Generic | Capacitor
C7 | 100pF | C_CHIP-0603(1608-METRIC) | CAPC1608X85 | Capacitor - Generic | Capacitor
C8 | 0.1uF | C_CHIP-0805(2012-METRIC) | CAPC2012X110 | Capacitor - Generic | Capacitor
C9 | 0.1uF | C_CHIP-0805(2012-METRIC) | CAPC2012X110 | Capacitor - Generic | Capacitor
C10 | 1uF | C_CHIP-0805(2012-METRIC) | CAPC2012X110 | Capacitor - Generic | Capacitor
C11 | 0.1uF | C_CHIP-0805(2012-METRIC) | CAPC2012X110 | Capacitor - Generic | Capacitor
C12 | 1uF | C_CHIP-0805(2012-METRIC) | CAPC2012X110 | Capacitor - Generic | Capacitor
C13 | 0.1uF | C_CHIP-0805(2012-METRIC) | CAPC2012X110 | Capacitor - Generic | Capacitor
C14 | 10uF | 293D106X0016A2TE3CAP_293D-A_VSS | CAP_293D-A_VSS |  |  | Copyright (C) 2023 Ultra Librarian. All rights reserved. |  |  |  |  |  | 293D106X0016A2TE3 | Vishay
C15 | 1uF | C_CHIP-0805(2012-METRIC) | CAPC2012X110 | Capacitor - Generic | Capacitor
C16 | 0.1uF | C_CHIP-0805(2012-METRIC) | CAPC2012X110 | Capacitor - Generic | Capacitor
C17 | 1uF | C_CHIP-0805(2012-METRIC) | CAPC2012X110 | Capacitor - Generic | Capacitor
C18 | 10uF | 293D106X0016A2TE3CAP_293D-A_VSS | CAP_293D-A_VSS |  |  | Copyright (C) 2023 Ultra Librarian. All rights reserved. |  |  |  |  |  | 293D106X0016A2TE3 | Vishay
C19 | 1uF | C_CHIP-0805(2012-METRIC) | CAPC2012X110 | Capacitor - Generic | Capacitor
C20 | 0.1uF | C_CHIP-0805(2012-METRIC) | CAPC2012X110 | Capacitor - Generic | Capacitor
C21 | 2.2uF | C_CHIP-0603(1608-METRIC) | CAPC1608X85 | Capacitor - Generic | Capacitor
C22 | 1uF | C_CHIP-0805(2012-METRIC) | CAPC2012X110 | Capacitor - Generic | Capacitor
C23 | 0.1uF | C_CHIP-0805(2012-METRIC) | CAPC2012X110 | Capacitor - Generic | Capacitor
C24 | 1.5nF | C_CHIP-0603(1608-METRIC) | CAPC1608X85 | Capacitor - Generic | Capacitor
C25 | 100pF | C_CHIP-0603(1608-METRIC) | CAPC1608X85 | Capacitor - Generic | Capacitor
C26 | 1uF | C_CHIP-0805(2012-METRIC) | CAPC2012X110 | Capacitor - Generic | Capacitor
C27 | 0.1uF | C_CHIP-0805(2012-METRIC) | CAPC2012X110 | Capacitor - Generic | Capacitor
C28 | 1uF | C_CHIP-0805(2012-METRIC) | CAPC2012X110 | Capacitor - Generic | Capacitor
C29 | 0.1uF | C_CHIP-0805(2012-METRIC) | CAPC2012X110 | Capacitor - Generic | Capacitor
C30 | 10uF | 293D106X0016A2TE3CAP_293D-A_VSS | CAP_293D-A_VSS |  |  | Copyright (C) 2023 Ultra Librarian. All rights reserved. |  |  |  |  |  | 293D106X0016A2TE3 | Vishay
C31 | 1uF | C_CHIP-0805(2012-METRIC) | CAPC2012X110 | Capacitor - Generic | Capacitor
C32 | 0.1uF | C_CHIP-0805(2012-METRIC) | CAPC2012X110 | Capacitor - Generic | Capacitor
C33 | 1uF | C_CHIP-0805(2012-METRIC) | CAPC2012X110 | Capacitor - Generic | Capacitor
C34 | 1uF | C_CHIP-0805(2012-METRIC) | CAPC2012X110 | Capacitor - Generic | Capacitor
C35 | 10uF | 293D106X0016A2TE3CAP_293D-A_VSS | CAP_293D-A_VSS |  |  | Copyright (C) 2023 Ultra Librarian. All rights reserved. |  |  |  |  |  | 293D106X0016A2TE3 | Vishay
C36 | 1uF | C_CHIP-0805(2012-METRIC) | CAPC2012X110 | Capacitor - Generic | Capacitor
C37 | 0.1uF | C_CHIP-0805(2012-METRIC) | CAPC2012X110 | Capacitor - Generic | Capacitor
C38 | 1uF | C_CHIP-0805(2012-METRIC) | CAPC2012X110 | Capacitor - Generic | Capacitor
C39 | 1uF | C_CHIP-0805(2012-METRIC) | CAPC2012X110 | Capacitor - Generic | Capacitor
C40 | 0.1uF | C_CHIP-0805(2012-METRIC) | CAPC2012X110 | Capacitor - Generic | Capacitor
C41 | 1.5nF | C_CHIP-0603(1608-METRIC) | CAPC1608X85 | Capacitor - Generic | Capacitor
C42 | 100pF | C_CHIP-0603(1608-METRIC) | CAPC1608X85 | Capacitor - Generic | Capacitor
C43 | 1uF | C_CHIP-0805(2012-METRIC) | CAPC2012X110 | Capacitor - Generic | Capacitor
C44 | 0.1uF | C_CHIP-0805(2012-METRIC) | CAPC2012X110 | Capacitor - Generic | Capacitor
C45 | 1uF | C_CHIP-0805(2012-METRIC) | CAPC2012X110 | Capacitor - Generic | Capacitor
C46 | 0.1uF | C_CHIP-0805(2012-METRIC) | CAPC2012X110 | Capacitor - Generic | Capacitor
C47 | 10uF | 293D106X0016A2TE3CAP_293D-A_VSS | CAP_293D-A_VSS |  |  | Copyright (C) 2023 Ultra Librarian. All rights reserved. |  |  |  |  |  | 293D106X0016A2TE3 | Vishay
C48 | 1uF | C_CHIP-0805(2012-METRIC) | CAPC2012X110 | Capacitor - Generic | Capacitor
C49 | 0.1uF | C_CHIP-0805(2012-METRIC) | CAPC2012X110 | Capacitor - Generic | Capacitor
C50 | 1uF | C_CHIP-0805(2012-METRIC) | CAPC2012X110 | Capacitor - Generic | Capacitor
C51 | 10uF | 293D106X0016A2TE3CAP_293D-A_VSS | CAP_293D-A_VSS |  |  | Copyright (C) 2023 Ultra Librarian. All rights reserved. |  |  |  |  |  | 293D106X0016A2TE3 | Vishay
C52 | 1uF | C_CHIP-0805(2012-METRIC) | CAPC2012X110 | Capacitor - Generic | Capacitor
C53 | 0.1uF | C_CHIP-0805(2012-METRIC) | CAPC2012X110 | Capacitor - Generic | Capacitor
C54 | 1.5nF | C_CHIP-0603(1608-METRIC) | CAPC1608X85 | Capacitor - Generic | Capacitor
C55 | 1uF | C_CHIP-0805(2012-METRIC) | CAPC2012X110 | Capacitor - Generic | Capacitor
C56 | 0.1uF | C_CHIP-0805(2012-METRIC) | CAPC2012X110 | Capacitor - Generic | Capacitor
C57 | 0.1uF | C_CHIP-0805(2012-METRIC) | CAPC2012X110 | Capacitor - Generic | Capacitor
C58 | 1uF | C_CHIP-0805(2012-METRIC) | CAPC2012X110 | Capacitor - Generic | Capacitor
C59 | 0.1uF | C_CHIP-0805(2012-METRIC) | CAPC2012X110 | Capacitor - Generic | Capacitor
C60 | 10uF | 293D106X0016A2TE3CAP_293D-A_VSS | CAP_293D-A_VSS |  |  | Copyright (C) 2023 Ultra Librarian. All rights reserved. |  |  |  |  |  | 293D106X0016A2TE3 | Vishay
C61 | 1uF | C_CHIP-0805(2012-METRIC) | CAPC2012X110 | Capacitor - Generic | Capacitor
C62 | 0.1uF | C_CHIP-0805(2012-METRIC) | CAPC2012X110 | Capacitor - Generic | Capacitor
C63 | 1uF | C_CHIP-0805(2012-METRIC) | CAPC2012X110 | Capacitor - Generic | Capacitor
C64 | 10uF | 293D106X0016A2TE3CAP_293D-A_VSS | CAP_293D-A_VSS |  |  | Copyright (C) 2023 Ultra Librarian. All rights reserved. |  |  |  |  |  | 293D106X0016A2TE3 | Vishay
C65 | 0.1uF | C_CHIP-0805(2012-METRIC) | CAPC2012X110 | Capacitor - Generic | Capacitor
C66 | 1uF | C_CHIP-0805(2012-METRIC) | CAPC2012X110 | Capacitor - Generic | Capacitor
C67 | 1.5nF | C_CHIP-0603(1608-METRIC) | CAPC1608X85 | Capacitor - Generic | Capacitor
C68 | 100pF | C_CHIP-0603(1608-METRIC) | CAPC1608X85 | Capacitor - Generic | Capacitor
C69 | 1uF | C_CHIP-0805(2012-METRIC) | CAPC2012X110 | Capacitor - Generic | Capacitor
C70 | 0.1uF | C_CHIP-0805(2012-METRIC) | CAPC2012X110 | Capacitor - Generic | Capacitor
C71 | 1uF | C_CHIP-0805(2012-METRIC) | CAPC2012X110 | Capacitor - Generic | Capacitor
C72 | 0.1uF | C_CHIP-0805(2012-METRIC) | CAPC2012X110 | Capacitor - Generic | Capacitor
C73 | 10uF | 293D106X0016A2TE3CAP_293D-A_VSS | CAP_293D-A_VSS |  |  | Copyright (C) 2023 Ultra Librarian. All rights reserved. |  |  |  |  |  | 293D106X0016A2TE3 | Vishay
C74 | 1uF | C_CHIP-0805(2012-METRIC) | CAPC2012X110 | Capacitor - Generic | Capacitor
C75 | 0.1uF | C_CHIP-0805(2012-METRIC) | CAPC2012X110 | Capacitor - Generic | Capacitor
C76 | 1uF | C_CHIP-0805(2012-METRIC) | CAPC2012X110 | Capacitor - Generic | Capacitor
C77 | 10uF | 293D106X0016A2TE3CAP_293D-A_VSS | CAP_293D-A_VSS |  |  | Copyright (C) 2023 Ultra Librarian. All rights reserved. |  |  |  |  |  | 293D106X0016A2TE3 | Vishay
C78 | 0.1uF | C_CHIP-0805(2012-METRIC) | CAPC2012X110 | Capacitor - Generic | Capacitor
C79 | 0.1uF | C_CHIP-0805(2012-METRIC) | CAPC2012X110 | Capacitor - Generic | Capacitor
C80 | 0.1uF | C_CHIP-0805(2012-METRIC) | CAPC2012X110 | Capacitor - Generic | Capacitor
C81 | 1uF | C_CHIP-0805(2012-METRIC) | CAPC2012X110 | Capacitor - Generic | Capacitor
C82 | 0.1uF | C_CHIP-0805(2012-METRIC) | CAPC2012X110 | Capacitor - Generic | Capacitor
C83 | 1.5nF | C_CHIP-0603(1608-METRIC) | CAPC1608X85 | Capacitor - Generic | Capacitor
C84 | 100pF | C_CHIP-0603(1608-METRIC) | CAPC1608X85 | Capacitor - Generic | Capacitor
C85 | 10uF | 293D106X0016A2TE3CAP_293D-A_VSS | CAP_293D-A_VSS |  |  | Copyright (C) 2023 Ultra Librarian. All rights reserved. |  |  |  |  |  | 293D106X0016A2TE3 | Vishay
C86 | 10uF | 293D106X0016A2TE3CAP_293D-A_VSS | CAP_293D-A_VSS |  |  | Copyright (C) 2023 Ultra Librarian. All rights reserved. |  |  |  |  |  | 293D106X0016A2TE3 | Vishay
C87 | 2.2uF | C_CHIP-0603(1608-METRIC) | CAPC1608X85 | Capacitor - Generic | Capacitor
C88 | 0.1uF | C_CHIP-0805(2012-METRIC) | CAPC2012X110 | Capacitor - Generic | Capacitor
C89 | 2.2uF | C_CHIP-0603(1608-METRIC) | CAPC1608X85 | Capacitor - Generic | Capacitor
C90 | 0.1uF | C_CHIP-0805(2012-METRIC) | CAPC2012X110 | Capacitor - Generic | Capacitor
C91 | 1uF | C_CHIP-0805(2012-METRIC) | CAPC2012X110 | Capacitor - Generic | Capacitor
C92 | 0.1uF | C_CHIP-0805(2012-METRIC) | CAPC2012X110 | Capacitor - Generic | Capacitor
C93 | 1.5nF | C_CHIP-0603(1608-METRIC) | CAPC1608X85 | Capacitor - Generic | Capacitor
C94 | 100pF | C_CHIP-0603(1608-METRIC) | CAPC1608X85 | Capacitor - Generic | Capacitor
C95 | 0.1uF | C_CHIP-0805(2012-METRIC) | CAPC2012X110 | Capacitor - Generic | Capacitor
C96 | 2.2uF | C_CHIP-0603(1608-METRIC) | CAPC1608X85 | Capacitor - Generic | Capacitor
C97 | 1uF | C_CHIP-0805(2012-METRIC) | CAPC2012X110 | Capacitor - Generic | Capacitor
C98 | 0.01uF | C_CHIP-0805(2012-METRIC) | CAPC2012X110 | Capacitor - Generic | Capacitor
C99 | 0.1uF | C_CHIP-0805(2012-METRIC) | CAPC2012X110 | Capacitor - Generic | Capacitor
C100 | 2.2uF | C_CHIP-0603(1608-METRIC) | CAPC1608X85 | Capacitor - Generic | Capacitor
C101 | 22uF | C_TANTALUM-1206(3216-METRIC) | CAPM3216X180 | Capacitor - Generic | Capacitor
C102 | 22uF | C_TANTALUM-1206(3216-METRIC) | CAPM3216X180 | Capacitor - Generic | Capacitor
C103 | CKCL44X7R1H102M085AACKCL44_TDK-L | CKCL44X7R1H102M085AACKCL44_TDK-L | CKCL44_TDK-L |  |  | Copyright (C) 2023 Ultra Librarian. All rights reserved. |  |  |  |  |  | CKCL44X7R1H102M085AA | TDK
C104 | CKCL44X7R1H102M085AACKCL44_TDK-L | CKCL44X7R1H102M085AACKCL44_TDK-L | CKCL44_TDK-L |  |  | Copyright (C) 2023 Ultra Librarian. All rights reserved. |  |  |  |  |  | CKCL44X7R1H102M085AA | TDK
C105 | 0.1uF | C_CHIP-0805(2012-METRIC) | CAPC2012X110 | Capacitor - Generic | Capacitor
C106 | CKCL44X7R1H102M085AACKCL44_TDK-L | CKCL44X7R1H102M085AACKCL44_TDK-L | CKCL44_TDK-L |  |  | Copyright (C) 2023 Ultra Librarian. All rights reserved. |  |  |  |  |  | CKCL44X7R1H102M085AA | TDK
C107 | CKCL44X7R1H102M085AACKCL44_TDK-L | CKCL44X7R1H102M085AACKCL44_TDK-L | CKCL44_TDK-L |  |  | Copyright (C) 2023 Ultra Librarian. All rights reserved. |  |  |  |  |  | CKCL44X7R1H102M085AA | TDK
C108 | CKCL44X7R1H102M085AACKCL44_TDK-L | CKCL44X7R1H102M085AACKCL44_TDK-L | CKCL44_TDK-L |  |  | Copyright (C) 2023 Ultra Librarian. All rights reserved. |  |  |  |  |  | CKCL44X7R1H102M085AA | TDK
C109 | CKCL44X7R1H102M085AACKCL44_TDK-L | CKCL44X7R1H102M085AACKCL44_TDK-L | CKCL44_TDK-L |  |  | Copyright (C) 2023 Ultra Librarian. All rights reserved. |  |  |  |  |  | CKCL44X7R1H102M085AA | TDK
C110 | CKCL44X7R1H102M085AACKCL44_TDK-L | CKCL44X7R1H102M085AACKCL44_TDK-L | CKCL44_TDK-L |  |  | Copyright (C) 2023 Ultra Librarian. All rights reserved. |  |  |  |  |  | CKCL44X7R1H102M085AA | TDK
C111 | 0.1uF | C_CHIP-0805(2012-METRIC) | CAPC2012X110 | Capacitor - Generic | Capacitor
C112 | 0.1uF | C_CHIP-0805(2012-METRIC) | CAPC2012X110 | Capacitor - Generic | Capacitor
C113 | 0.1uF | C_CHIP-0805(2012-METRIC) | CAPC2012X110 | Capacitor - Generic | Capacitor
C114 | 15pF | C_CHIP-0603(1608-METRIC) | CAPC1608X85 | Capacitor - Generic | Capacitor
C115 | 15pF | C_CHIP-0603(1608-METRIC) | CAPC1608X85 | Capacitor - Generic | Capacitor
C116 | 0.1uF | C_CHIP-0805(2012-METRIC) | CAPC2012X110 | Capacitor - Generic | Capacitor
C117 | 0.1uF | C_CHIP-0805(2012-METRIC) | CAPC2012X110 | Capacitor - Generic | Capacitor
C118 | 1uF | C_CHIP-0805(2012-METRIC) | CAPC2012X110 | Capacitor - Generic | Capacitor
C119 | 1uF | C_CHIP-0805(2012-METRIC) | CAPC2012X110 | Capacitor - Generic | Capacitor
C120 | 1uF | C_CHIP-0805(2012-METRIC) | CAPC2012X110 | Capacitor - Generic | Capacitor
C121 | 1uF | C_CHIP-0805(2012-METRIC) | CAPC2012X110 | Capacitor - Generic | Capacitor
C122 | 22uF | C_TANTALUM-1206(3216-METRIC) | CAPM3216X180 | Capacitor - Generic | Capacitor
C123 | 0.1uF | C_CHIP-0805(2012-METRIC) | CAPC2012X110 | Capacitor - Generic | Capacitor
C124 | 0.1uF | C_CHIP-0805(2012-METRIC) | CAPC2012X110 | Capacitor - Generic | Capacitor
C125 | 1uF | C_CHIP-0805(2012-METRIC) | CAPC2012X110 | Capacitor - Generic | Capacitor
C126 | CKCL44X7R1H102M085AACKCL44_TDK-L | CKCL44X7R1H102M085AACKCL44_TDK-L | CKCL44_TDK-L |  |  | Copyright (C) 2023 Ultra Librarian. All rights reserved. |  |  |  |  |  | CKCL44X7R1H102M085AA | TDK
C127 | CKCL44X7R1H102M085AACKCL44_TDK-L | CKCL44X7R1H102M085AACKCL44_TDK-L | CKCL44_TDK-L |  |  | Copyright (C) 2023 Ultra Librarian. All rights reserved. |  |  |  |  |  | CKCL44X7R1H102M085AA | TDK
C128 | CKCL44X7R1H102M085AACKCL44_TDK-L | CKCL44X7R1H102M085AACKCL44_TDK-L | CKCL44_TDK-L |  |  | Copyright (C) 2023 Ultra Librarian. All rights reserved. |  |  |  |  |  | CKCL44X7R1H102M085AA | TDK
C129 | CKCL44X7R1H102M085AACKCL44_TDK-L | CKCL44X7R1H102M085AACKCL44_TDK-L | CKCL44_TDK-L |  |  | Copyright (C) 2023 Ultra Librarian. All rights reserved. |  |  |  |  |  | CKCL44X7R1H102M085AA | TDK
C130 | CKCL44X7R1H102M085AACKCL44_TDK-L | CKCL44X7R1H102M085AACKCL44_TDK-L | CKCL44_TDK-L |  |  | Copyright (C) 2023 Ultra Librarian. All rights reserved. |  |  |  |  |  | CKCL44X7R1H102M085AA | TDK
C131 | CKCL44X7R1H102M085AACKCL44_TDK-L | CKCL44X7R1H102M085AACKCL44_TDK-L | CKCL44_TDK-L |  |  | Copyright (C) 2023 Ultra Librarian. All rights reserved. |  |  |  |  |  | CKCL44X7R1H102M085AA | TDK
C132 | 2.2uF | C_CHIP-0603(1608-METRIC) | CAPC1608X85 | Capacitor - Generic | Capacitor
C133 | 0.1uF | C_CHIP-0805(2012-METRIC) | CAPC2012X110 | Capacitor - Generic | Capacitor
C134 | 0.1uF | C_CHIP-0805(2012-METRIC) | CAPC2012X110 | Capacitor - Generic | Capacitor
C135 | 0.1uF | C_CHIP-0805(2012-METRIC) | CAPC2012X110 | Capacitor - Generic | Capacitor
C136 | 22uF | C_TANTALUM-1206(3216-METRIC) | CAPM3216X180 | Capacitor - Generic | Capacitor
C137 | 0.1uF | C_CHIP-0805(2012-METRIC) | CAPC2012X110 | Capacitor - Generic | Capacitor
C138 | 1uF | C_CHIP-0805(2012-METRIC) | CAPC2012X110 | Capacitor - Generic | Capacitor
C139 | 1uF | C_CHIP-0805(2012-METRIC) | CAPC2012X110 | Capacitor - Generic | Capacitor
C140 | 1uF | C_CHIP-0805(2012-METRIC) | CAPC2012X110 | Capacitor - Generic | Capacitor
C141 | 1uF | C_CHIP-0805(2012-METRIC) | CAPC2012X110 | Capacitor - Generic | Capacitor
C142 | 1uF | C_CHIP-0805(2012-METRIC) | CAPC2012X110 | Capacitor - Generic | Capacitor
C143 | 0.1uF | C_CHIP-0805(2012-METRIC) | CAPC2012X110 | Capacitor - Generic | Capacitor
C144 | 1uF | C_CHIP-0805(2012-METRIC) | CAPC2012X110 | Capacitor - Generic | Capacitor
C145 | 1uF | C_CHIP-0805(2012-METRIC) | CAPC2012X110 | Capacitor - Generic | Capacitor
C146 | 1uF | C_CHIP-0805(2012-METRIC) | CAPC2012X110 | Capacitor - Generic | Capacitor
C147 | 1uF | C_CHIP-0805(2012-METRIC) | CAPC2012X110 | Capacitor - Generic | Capacitor
C148 | 1uF | C_CHIP-0805(2012-METRIC) | CAPC2012X110 | Capacitor - Generic | Capacitor
C149 | 1uF | C_CHIP-0805(2012-METRIC) | CAPC2012X110 | Capacitor - Generic | Capacitor
C150 | 0.1uF | C_CHIP-0805(2012-METRIC) | CAPC2012X110 | Capacitor - Generic | Capacitor
C151 | 0.1uF | C_CHIP-0805(2012-METRIC) | CAPC2012X110 | Capacitor - Generic | Capacitor
C152 | 1uF | C_CHIP-0805(2012-METRIC) | CAPC2012X110 | Capacitor - Generic | Capacitor
C153 | 22uF | C_TANTALUM-1206(3216-METRIC) | CAPM3216X180 | Capacitor - Generic | Capacitor
C154 | 22uF | C_TANTALUM-1206(3216-METRIC) | CAPM3216X180 | Capacitor - Generic | Capacitor
C155 | 0.1uF | C_CHIP-0805(2012-METRIC) | CAPC2012X110 | Capacitor - Generic | Capacitor
C156 | 1uF | C_CHIP-0805(2012-METRIC) | CAPC2012X110 | Capacitor - Generic | Capacitor
C157 | 0.1uF | C_CHIP-0805(2012-METRIC) | CAPC2012X110 | Capacitor - Generic | Capacitor
C158 | 1uF | C_CHIP-0805(2012-METRIC) | CAPC2012X110 | Capacitor - Generic | Capacitor
C159 | 0.1uF | C_CHIP-0805(2012-METRIC) | CAPC2012X110 | Capacitor - Generic | Capacitor
C160 | 1uF | C_CHIP-0805(2012-METRIC) | CAPC2012X110 | Capacitor - Generic | Capacitor
C161 | 0.1uF | C_CHIP-0805(2012-METRIC) | CAPC2012X110 | Capacitor - Generic | Capacitor
C162 | 1uF | C_CHIP-0805(2012-METRIC) | CAPC2012X110 | Capacitor - Generic | Capacitor
C163 | 0.1uF | C_CHIP-0805(2012-METRIC) | CAPC2012X110 | Capacitor - Generic | Capacitor
C164 | 1uF | C_CHIP-0805(2012-METRIC) | CAPC2012X110 | Capacitor - Generic | Capacitor
C165 | 0.1uF | C_CHIP-0805(2012-METRIC) | CAPC2012X110 | Capacitor - Generic | Capacitor
C166 | 1uF | C_CHIP-0805(2012-METRIC) | CAPC2012X110 | Capacitor - Generic | Capacitor
C167 | 0.1uF | C_CHIP-0805(2012-METRIC) | CAPC2012X110 | Capacitor - Generic | Capacitor
C168 | 1uF | C_CHIP-0805(2012-METRIC) | CAPC2012X110 | Capacitor - Generic | Capacitor
C169 | 0.1uF | C_CHIP-0805(2012-METRIC) | CAPC2012X110 | Capacitor - Generic | Capacitor
C170 | 1uF | C_CHIP-0805(2012-METRIC) | CAPC2012X110 | Capacitor - Generic | Capacitor
C171 | 0.1uF | C_CHIP-0805(2012-METRIC) | CAPC2012X110 | Capacitor - Generic | Capacitor
C172 | 1uF | C_CHIP-0805(2012-METRIC) | CAPC2012X110 | Capacitor - Generic | Capacitor
C173 | 0.1uF | C_CHIP-0805(2012-METRIC) | CAPC2012X110 | Capacitor - Generic | Capacitor
C174 | 1uF | C_CHIP-0805(2012-METRIC) | CAPC2012X110 | Capacitor - Generic | Capacitor
C175 | 0.1uF | C_CHIP-0805(2012-METRIC) | CAPC2012X110 | Capacitor - Generic | Capacitor
C176 | 1uF | C_CHIP-0805(2012-METRIC) | CAPC2012X110 | Capacitor - Generic | Capacitor
C177 | 0.1uF | C_CHIP-0805(2012-METRIC) | CAPC2012X110 | Capacitor - Generic | Capacitor
C178 | 1uF | C_CHIP-0805(2012-METRIC) | CAPC2012X110 | Capacitor - Generic | Capacitor
C179 | 0.1uF | C_CHIP-0805(2012-METRIC) | CAPC2012X110 | Capacitor - Generic | Capacitor
C180 | 1uF | C_CHIP-0805(2012-METRIC) | CAPC2012X110 | Capacitor - Generic | Capacitor
C181 | 0.1uF | C_CHIP-0805(2012-METRIC) | CAPC2012X110 | Capacitor - Generic | Capacitor
C182 | 1uF | C_CHIP-0805(2012-METRIC) | CAPC2012X110 | Capacitor - Generic | Capacitor
C183 | 0.1uF | C_CHIP-0805(2012-METRIC) | CAPC2012X110 | Capacitor - Generic | Capacitor
C184 | 1uF | C_CHIP-0805(2012-METRIC) | CAPC2012X110 | Capacitor - Generic | Capacitor
C185 | 0.1uF | C_CHIP-0805(2012-METRIC) | CAPC2012X110 | Capacitor - Generic | Capacitor
C186 | 1uF | C_CHIP-0805(2012-METRIC) | CAPC2012X110 | Capacitor - Generic | Capacitor
C187 | 0.1uF | C_CHIP-0805(2012-METRIC) | CAPC2012X110 | Capacitor - Generic | Capacitor
C188 | 1uF | C_CHIP-0805(2012-METRIC) | CAPC2012X110 | Capacitor - Generic | Capacitor
C189 | 0.1uF | C_CHIP-0805(2012-METRIC) | CAPC2012X110 | Capacitor - Generic | Capacitor
C190 | 1uF | C_CHIP-0805(2012-METRIC) | CAPC2012X110 | Capacitor - Generic | Capacitor
C191 | 0.1uF | C_CHIP-0805(2012-METRIC) | CAPC2012X110 | Capacitor - Generic | Capacitor
C192 | 1uF | C_CHIP-0805(2012-METRIC) | CAPC2012X110 | Capacitor - Generic | Capacitor
C193 | 0.1uF | C_CHIP-0805(2012-METRIC) | CAPC2012X110 | Capacitor - Generic | Capacitor
C194 | 1uF | C_CHIP-0805(2012-METRIC) | CAPC2012X110 | Capacitor - Generic | Capacitor
C195 | 0.1uF | C_CHIP-0805(2012-METRIC) | CAPC2012X110 | Capacitor - Generic | Capacitor
C196 | 1uF | C_CHIP-0805(2012-METRIC) | CAPC2012X110 | Capacitor - Generic | Capacitor
C197 | 0.1uF | C_CHIP-0805(2012-METRIC) | CAPC2012X110 | Capacitor - Generic | Capacitor
C198 | 1uF | C_CHIP-0805(2012-METRIC) | CAPC2012X110 | Capacitor - Generic | Capacitor
C199 | 0.1uF | C_CHIP-0805(2012-METRIC) | CAPC2012X110 | Capacitor - Generic | Capacitor
C200 | 1uF | C_CHIP-0805(2012-METRIC) | CAPC2012X110 | Capacitor - Generic | Capacitor
C201 | 0.1uF | C_CHIP-0805(2012-METRIC) | CAPC2012X110 | Capacitor - Generic | Capacitor
C202 | 1uF | C_CHIP-0805(2012-METRIC) | CAPC2012X110 | Capacitor - Generic | Capacitor
C203 | 0.1uF | C_CHIP-0805(2012-METRIC) | CAPC2012X110 | Capacitor - Generic | Capacitor
C204 | 1uF | C_CHIP-0805(2012-METRIC) | CAPC2012X110 | Capacitor - Generic | Capacitor
C205 | 0.1uF | C_CHIP-0805(2012-METRIC) | CAPC2012X110 | Capacitor - Generic | Capacitor
C206 | 1uF | C_CHIP-0805(2012-METRIC) | CAPC2012X110 | Capacitor - Generic | Capacitor
C207 | 0.1uF | C_CHIP-0805(2012-METRIC) | CAPC2012X110 | Capacitor - Generic | Capacitor
C208 | 1uF | C_CHIP-0805(2012-METRIC) | CAPC2012X110 | Capacitor - Generic | Capacitor
C209 | 0.1uF | C_CHIP-0805(2012-METRIC) | CAPC2012X110 | Capacitor - Generic | Capacitor
C210 | 1uF | C_CHIP-0805(2012-METRIC) | CAPC2012X110 | Capacitor - Generic | Capacitor
C211 | 0.1uF | C_CHIP-0805(2012-METRIC) | CAPC2012X110 | Capacitor - Generic | Capacitor
C212 | 1uF | C_CHIP-0805(2012-METRIC) | CAPC2012X110 | Capacitor - Generic | Capacitor
C213 | 0.1uF | C_CHIP-0805(2012-METRIC) | CAPC2012X110 | Capacitor - Generic | Capacitor
C214 | 1uF | C_CHIP-0805(2012-METRIC) | CAPC2012X110 | Capacitor - Generic | Capacitor
C215 | 0.1uF | C_CHIP-0805(2012-METRIC) | CAPC2012X110 | Capacitor - Generic | Capacitor
C216 | 1uF | C_CHIP-0805(2012-METRIC) | CAPC2012X110 | Capacitor - Generic | Capacitor
C217 | 0.1uF | C_CHIP-0805(2012-METRIC) | CAPC2012X110 | Capacitor - Generic | Capacitor
C218 | 1uF | C_CHIP-0805(2012-METRIC) | CAPC2012X110 | Capacitor - Generic | Capacitor
C219 | 0.1uF | C_CHIP-0805(2012-METRIC) | CAPC2012X110 | Capacitor - Generic | Capacitor
C220 | 1uF | C_CHIP-0805(2012-METRIC) | CAPC2012X110 | Capacitor - Generic | Capacitor
C221 | 0.1uF | C_CHIP-0805(2012-METRIC) | CAPC2012X110 | Capacitor - Generic | Capacitor
C222 | 1uF | C_CHIP-0805(2012-METRIC) | CAPC2012X110 | Capacitor - Generic | Capacitor
C223 | 0.1uF | C_CHIP-0805(2012-METRIC) | CAPC2012X110 | Capacitor - Generic | Capacitor
C224 | 1uF | C_CHIP-0805(2012-METRIC) | CAPC2012X110 | Capacitor - Generic | Capacitor
C225 | 0.1uF | C_CHIP-0805(2012-METRIC) | CAPC2012X110 | Capacitor - Generic | Capacitor
C226 | 1uF | C_CHIP-0805(2012-METRIC) | CAPC2012X110 | Capacitor - Generic | Capacitor
C227 | 0.1uF | C_CHIP-0805(2012-METRIC) | CAPC2012X110 | Capacitor - Generic | Capacitor
C228 | 1uF | C_CHIP-0805(2012-METRIC) | CAPC2012X110 | Capacitor - Generic | Capacitor
C229 | 0.1uF | C_CHIP-0805(2012-METRIC) | CAPC2012X110 | Capacitor - Generic | Capacitor
C230 | 1uF | C_CHIP-0805(2012-METRIC) | CAPC2012X110 | Capacitor - Generic | Capacitor
C231 | 0.1uF | C_CHIP-0805(2012-METRIC) | CAPC2012X110 | Capacitor - Generic | Capacitor
C232 | 1uF | C_CHIP-0805(2012-METRIC) | CAPC2012X110 | Capacitor - Generic | Capacitor
C233 | 0.1uF | C_CHIP-0805(2012-METRIC) | CAPC2012X110 | Capacitor - Generic | Capacitor
C234 | 1uF | C_CHIP-0805(2012-METRIC) | CAPC2012X110 | Capacitor - Generic | Capacitor
C235 | 0.1uF | C_CHIP-0805(2012-METRIC) | CAPC2012X110 | Capacitor - Generic | Capacitor
C236 | 1uF | C_CHIP-0805(2012-METRIC) | CAPC2012X110 | Capacitor - Generic | Capacitor
C237 | 0.1uF | C_CHIP-0805(2012-METRIC) | CAPC2012X110 | Capacitor - Generic | Capacitor
C238 | 1uF | C_CHIP-0805(2012-METRIC) | CAPC2012X110 | Capacitor - Generic | Capacitor
C239 | 0.1uF | C_CHIP-0805(2012-METRIC) | CAPC2012X110 | Capacitor - Generic | Capacitor
C240 | 1uF | C_CHIP-0805(2012-METRIC) | CAPC2012X110 | Capacitor - Generic | Capacitor
C241 | 0.1uF | C_CHIP-0805(2012-METRIC) | CAPC2012X110 | Capacitor - Generic | Capacitor
C242 | 1uF | C_CHIP-0805(2012-METRIC) | CAPC2012X110 | Capacitor - Generic | Capacitor
C243 | 0.1uF | C_CHIP-0805(2012-METRIC) | CAPC2012X110 | Capacitor - Generic | Capacitor
C244 | 1uF | C_CHIP-0805(2012-METRIC) | CAPC2012X110 | Capacitor - Generic | Capacitor
C245 | 0.1uF | C_CHIP-0805(2012-METRIC) | CAPC2012X110 | Capacitor - Generic | Capacitor
C246 | 1uF | C_CHIP-0805(2012-METRIC) | CAPC2012X110 | Capacitor - Generic | Capacitor
C247 | 0.1uF | C_CHIP-0805(2012-METRIC) | CAPC2012X110 | Capacitor - Generic | Capacitor
C248 | 1uF | C_CHIP-0805(2012-METRIC) | CAPC2012X110 | Capacitor - Generic | Capacitor
C250 | 0.1uF | C_CHIP-0805(2012-METRIC) | CAPC2012X110 | Capacitor - Generic | Capacitor
C251 | 1uF | C_CHIP-0805(2012-METRIC) | CAPC2012X110 | Capacitor - Generic | Capacitor
C252 | 0.1uF | C_CHIP-0805(2012-METRIC) | CAPC2012X110 | Capacitor - Generic | Capacitor
C253 | 1uF | C_CHIP-0805(2012-METRIC) | CAPC2012X110 | Capacitor - Generic | Capacitor
C254 | 0.1uF | C_CHIP-0805(2012-METRIC) | CAPC2012X110 | Capacitor - Generic | Capacitor
C255 | 1uF | C_CHIP-0805(2012-METRIC) | CAPC2012X110 | Capacitor - Generic | Capacitor
C256 | 0.1uF | C_CHIP-0805(2012-METRIC) | CAPC2012X110 | Capacitor - Generic | Capacitor
C257 | 1uF | C_CHIP-0805(2012-METRIC) | CAPC2012X110 | Capacitor - Generic | Capacitor
C258 | 0.1uF | C_CHIP-0805(2012-METRIC) | CAPC2012X110 | Capacitor - Generic | Capacitor
C259 | 1uF | C_CHIP-0805(2012-METRIC) | CAPC2012X110 | Capacitor - Generic | Capacitor
CR1 | BAT85,113DO-34_NEX | BAT85,113DO-34_NEX | DO-34_NEX |  |  | Copyright (C) 2023 Ultra Librarian. All rights reserved. |  |  |  |  |  | BAT85,113 | Nexperia
FB1 | FERRITE_BEAD | FBCHIP-0603(1608-METRIC) | BEADC1608X95N | Ferrite Bead - Generic | Filter |  |  |  |  |  |  |  |  |  |  |  |  |  |  |  |  |  |  |  | Ferrite bead |  |  |  |  |  |  | FERRITE_BEAD
FB2 | FERRITE_BEAD | FBCHIP-0603(1608-METRIC) | BEADC1608X95N | Ferrite Bead - Generic | Filter |  |  |  |  |  |  |  |  |  |  |  |  |  |  |  |  |  |  |  | Ferrite bead |  |  |  |  |  |  | FERRITE_BEAD
FB3 | FERRITE_BEAD | FBCHIP-0603(1608-METRIC) | BEADC1608X95N | Ferrite Bead - Generic | Filter |  |  |  |  |  |  |  |  |  |  |  |  |  |  |  |  |  |  |  | Ferrite bead |  |  |  |  |  |  | FERRITE_BEAD
FB4 | FERRITE_BEAD | FBCHIP-0603(1608-METRIC) | BEADC1608X95N | Ferrite Bead - Generic | Filter |  |  |  |  |  |  |  |  |  |  |  |  |  |  |  |  |  |  |  | Ferrite bead |  |  |  |  |  |  | FERRITE_BEAD
FB5 | FERRITE_BEAD | FBCHIP-0603(1608-METRIC) | BEADC1608X95N | Ferrite Bead - Generic | Filter |  |  |  |  |  |  |  |  |  |  |  |  |  |  |  |  |  |  |  | Ferrite bead |  |  |  |  |  |  | FERRITE_BEAD
FB6 | FERRITE_BEAD | FBCHIP-0603(1608-METRIC) | BEADC1608X95N | Ferrite Bead - Generic | Filter |  |  |  |  |  |  |  |  |  |  |  |  |  |  |  |  |  |  |  | Ferrite bead |  |  |  |  |  |  | FERRITE_BEAD
FB7 | FERRITE_BEAD | FBCHIP-0603(1608-METRIC) | BEADC1608X95N | Ferrite Bead - Generic | Filter |  |  |  |  |  |  |  |  |  |  |  |  |  |  |  |  |  |  |  | Ferrite bead |  |  |  |  |  |  | FERRITE_BEAD
FB8 | FERRITE_BEAD | FBCHIP-0603(1608-METRIC) | BEADC1608X95N | Ferrite Bead - Generic | Filter |  |  |  |  |  |  |  |  |  |  |  |  |  |  |  |  |  |  |  | Ferrite bead |  |  |  |  |  |  | FERRITE_BEAD
FB9 | FERRITE_BEAD | FBCHIP-0603(1608-METRIC) | BEADC1608X95N | Ferrite Bead - Generic | Filter |  |  |  |  |  |  |  |  |  |  |  |  |  |  |  |  |  |  |  | Ferrite bead |  |  |  |  |  |  | FERRITE_BEAD
FB10 | FERRITE_BEAD | FBCHIP-0603(1608-METRIC) | BEADC1608X95N | Ferrite Bead - Generic | Filter |  |  |  |  |  |  |  |  |  |  |  |  |  |  |  |  |  |  |  | Ferrite bead |  |  |  |  |  |  | FERRITE_BEAD
FB11 | FERRITE_BEAD | FBCHIP-0603(1608-METRIC) | BEADC1608X95N | Ferrite Bead - Generic | Filter |  |  |  |  |  |  |  |  |  |  |  |  |  |  |  |  |  |  |  | Ferrite bead |  |  |  |  |  |  | FERRITE_BEAD
FB12 | FERRITE_BEAD | FBCHIP-0603(1608-METRIC) | BEADC1608X95N | Ferrite Bead - Generic | Filter |  |  |  |  |  |  |  |  |  |  |  |  |  |  |  |  |  |  |  | Ferrite bead |  |  |  |  |  |  | FERRITE_BEAD
FB13 | FERRITE_BEAD | FBCHIP-0603(1608-METRIC) | BEADC1608X95N | Ferrite Bead - Generic | Filter |  |  |  |  |  |  |  |  |  |  |  |  |  |  |  |  |  |  |  | Ferrite bead |  |  |  |  |  |  | FERRITE_BEAD
FB14 | FERRITE_BEAD | FBCHIP-0603(1608-METRIC) | BEADC1608X95N | Ferrite Bead - Generic | Filter |  |  |  |  |  |  |  |  |  |  |  |  |  |  |  |  |  |  |  | Ferrite bead |  |  |  |  |  |  | FERRITE_BEAD
J1 | 3A/250V | B2B-XH-A | B2B-XH-A | XH Connector Top Entry - 2POS | CONNECTOR |  | 2.5mm pitch/disconnectable crimp style connector |  |  |  | JST (XH CONNECTOR) |  |  | B2B-XH-A |  | -25°C ~ 85°C |  | ACTIVE |  |  |  | COMPLIANT | B_B-XH-A |  |  |  | Through hole connector |  |  |  | top entry | 3A/250V
JP1 | PINHD-1X6/90 | PINHD-1X6/90 | 1X06/90 | PIN HEADER | CONNECTOR |  |  |  |  |  |  |  |  |  |  |  |  |  |  |  |  |  |  |  | PIN-HEADER
JP3 | PINHD-2X3/90 | PINHD-2X3/90 | 2X03/90 | PIN HEADER | CONNECTOR |  |  |  |  |  |  |  |  |  |  |  |  |  |  |  |  |  |  |  | PIN-HEADER
JP4 | PINHD-1X8/90 | PINHD-1X8/90 | 1X08/90 | PIN HEADER | CONNECTOR |  |  |  |  |  |  |  |  |  |  |  |  |  |  |  |  |  |  |  | PIN-HEADER
JP5 | PINHD-1X6/90 | PINHD-1X6/90 | 1X06/90 | PIN HEADER | CONNECTOR |  |  |  |  |  |  |  |  |  |  |  |  |  |  |  |  |  |  |  | PIN-HEADER
JP6 | PINHD-1X8/90 | PINHD-1X8/90 | 1X08/90 | PIN HEADER | CONNECTOR |  |  |  |  |  |  |  |  |  |  |  |  |  |  |  |  |  |  |  | PIN-HEADER
JP7 | PINHD-1X7/90 | PINHD-1X7/90 | 1X07/90 | PIN HEADER | CONNECTOR |  |  |  |  |  |  |  |  |  |  |  |  |  |  |  |  |  |  |  | PIN-HEADER
JP9 | PINHD-2X4/90 | PINHD-2X4/90 | 2X04/90 | PIN HEADER | CONNECTOR |  |  |  |  |  |  |  |  |  |  |  |  |  |  |  |  |  |  |  | PIN-HEADER
JP10 | PINHD-1X4 | PINHD-1X4 | 1X04 | PIN HEADER | CONNECTOR |  |  |  |  |  |  |  |  |  |  |  |  |  |  |  |  |  |  |  | PIN-HEADER
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

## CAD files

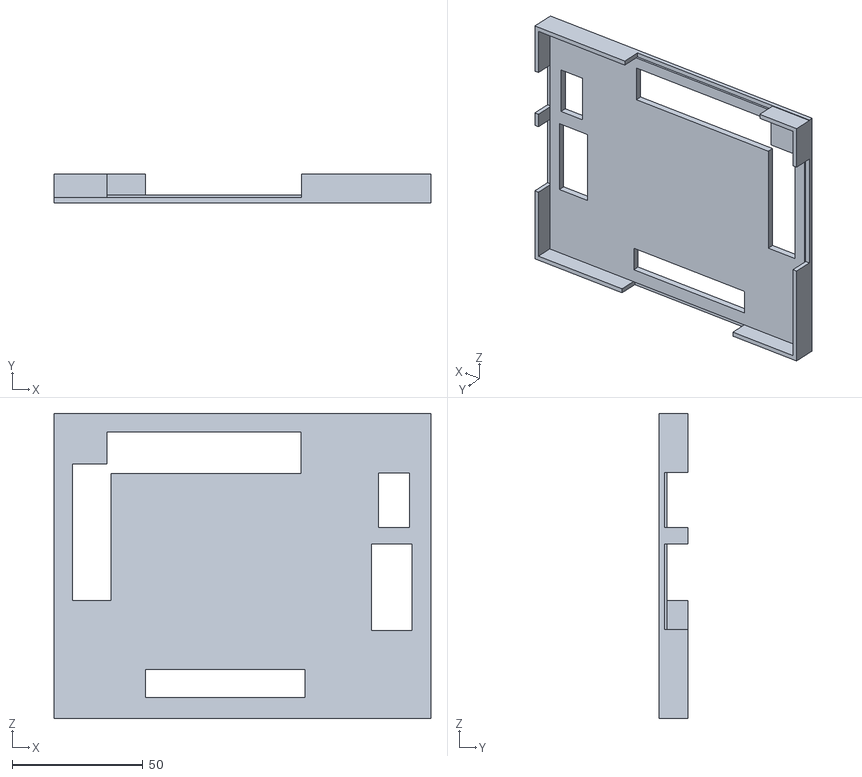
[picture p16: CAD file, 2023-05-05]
cad_files/Custom Board cover.stl
144.0 x 11.0 x 116.5

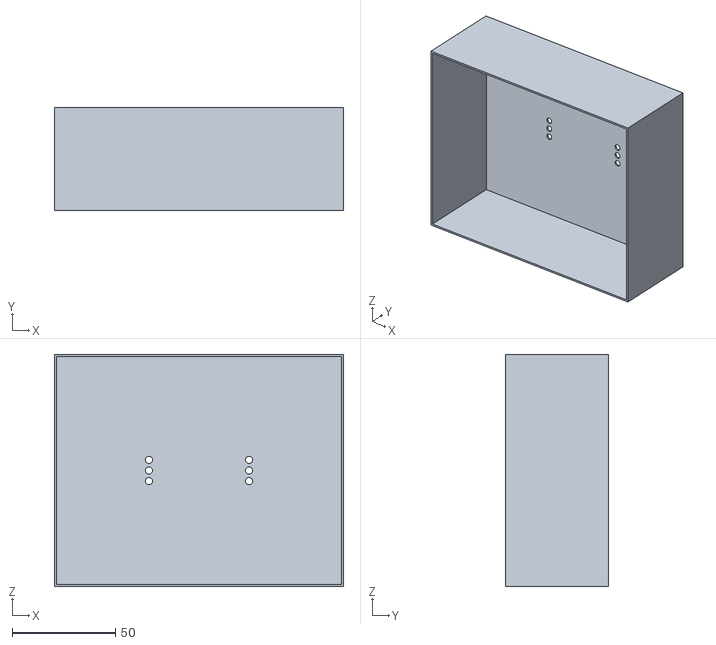
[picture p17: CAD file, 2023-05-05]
cad_files/Custom Board mount.stl
140.0 x 50.0 x 112.5

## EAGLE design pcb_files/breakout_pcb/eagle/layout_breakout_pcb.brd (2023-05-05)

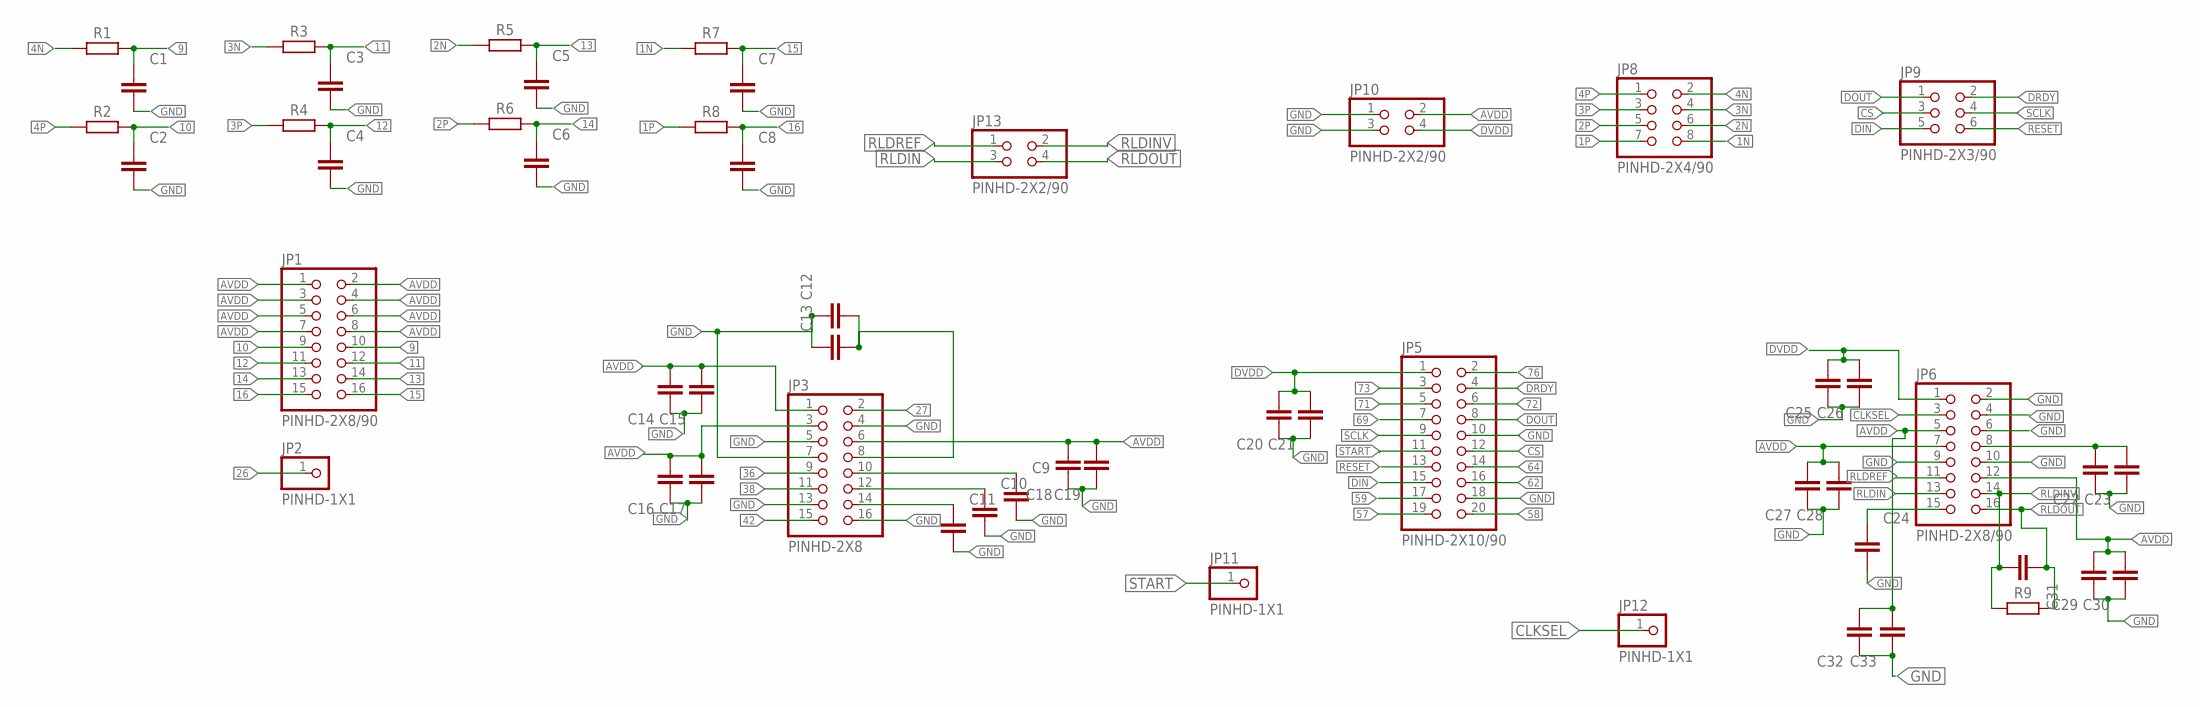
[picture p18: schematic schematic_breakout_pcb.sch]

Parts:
C1, C2, C3, C4, C5, C6, C7, C8, C9, C10, C11, C12, C13, C14, C15, C16, C17, C18, C19, C20, C21, C22, C23, C24, C25, C26, C27, C28, C29, C30, C31, C32, C33: C_TANTALUM-1206(3216-METRIC); CAPM3216X180
JP1, JP6: PINHD-2X8/90; 2X08/90
JP2, JP11, JP12: PINHD-1X1; 1X01
JP3: PINHD-2X8; 2X08
JP5: PINHD-2X10/90; 2X10/90
JP8: PINHD-2X4/90; 2X04/90
JP9: PINHD-2X3/90; 2X03/90
JP10, JP13: PINHD-2X2/90; 2X02/90
R1, R2, R3, R4, R5, R6, R7, R8, R9: R_CHIP-1206(3216-METRIC); RESC3216X70

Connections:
1N: JP8.8, R7.1
1P: JP8.7, R8.1
2N: JP8.6, R5.1
2P: JP8.5, R6.1
3N: JP8.4, R3.1
3P: JP8.3, R4.1
4N: JP8.2, R1.1
4P: JP8.1, R2.1
9: C1.1, JP1.10, R1.2
10: C2.1, JP1.9, R2.2
11: C3.1, JP1.12, R3.2
12: C4.1, JP1.11, R4.2
13: C5.1, JP1.14, R5.2
14: C6.1, JP1.13, R6.2
15: C7.1, JP1.16, R7.2
16: C8.1, JP1.15, R8.2
26: JP2.1
27: JP3.2
36: JP3.9
38: JP3.11
42: JP3.15
57: JP5.19
58: JP5.20
59: JP5.17
62: JP5.16
64: JP5.14
69: JP5.7
71: JP5.5
72: JP5.6
73: JP5.3
76: JP5.2
AVDD: C14.2, C15.2, C16.2, C17.2, C18.2, C19.2, C27.2, C28.2, C29.2, C30.2, C32.2, C33.2, JP1.1, JP1.2, JP1.3, JP1.4, JP1.5, JP1.6, JP1.7, JP1.8, JP3.1, JP3.3, JP3.6, JP6.5, JP6.7, JP6.12, JP10.2
CLKSEL: JP6.3, JP12.1
CS: JP5.12, JP9.3
DIN: JP5.15, JP9.5
DOUT: JP5.8, JP9.1
DRDY: JP5.4, JP9.2
DVDD: C20.2, C21.2, C25.2, C26.2, JP5.1, JP6.1, JP10.4
GND: C1.2, C2.2, C3.2, C4.2, C5.2, C6.2, C7.2, C8.2, C9.2, C10.2, C11.2, C12.1, C13.1, C14.1, C15.1, C16.1, C17.1, C18.1, C19.1, C20.1, C21.1, C22.1, C23.1, C24.2, C25.1, C26.1, C27.1, C28.1, C29.1, C30.1, C32.1, C33.1, JP3.4, JP3.5, JP3.7, JP3.13, JP3.16, JP5.10, JP5.18, JP6.2, JP6.4, JP6.6, JP6.9, JP6.10, JP10.1, JP10.3
unnamed: C9.1, JP3.10
unnamed: C10.1, JP3.12
unnamed: C11.1, JP3.14
unnamed: C12.2, C13.2, JP3.8
unnamed: C22.2, C23.2, JP6.8
unnamed: C24.1, JP6.15
RESET: JP5.13, JP9.6
RLDIN: JP6.13, JP13.3
RLDINV: C31.2, JP6.14, JP13.2, R9.1
RLDOUT: C31.1, JP6.16, JP13.4, R9.2
RLDREF: JP6.11, JP13.1
SCLK: JP5.9, JP9.4
START: JP5.11, JP11.1

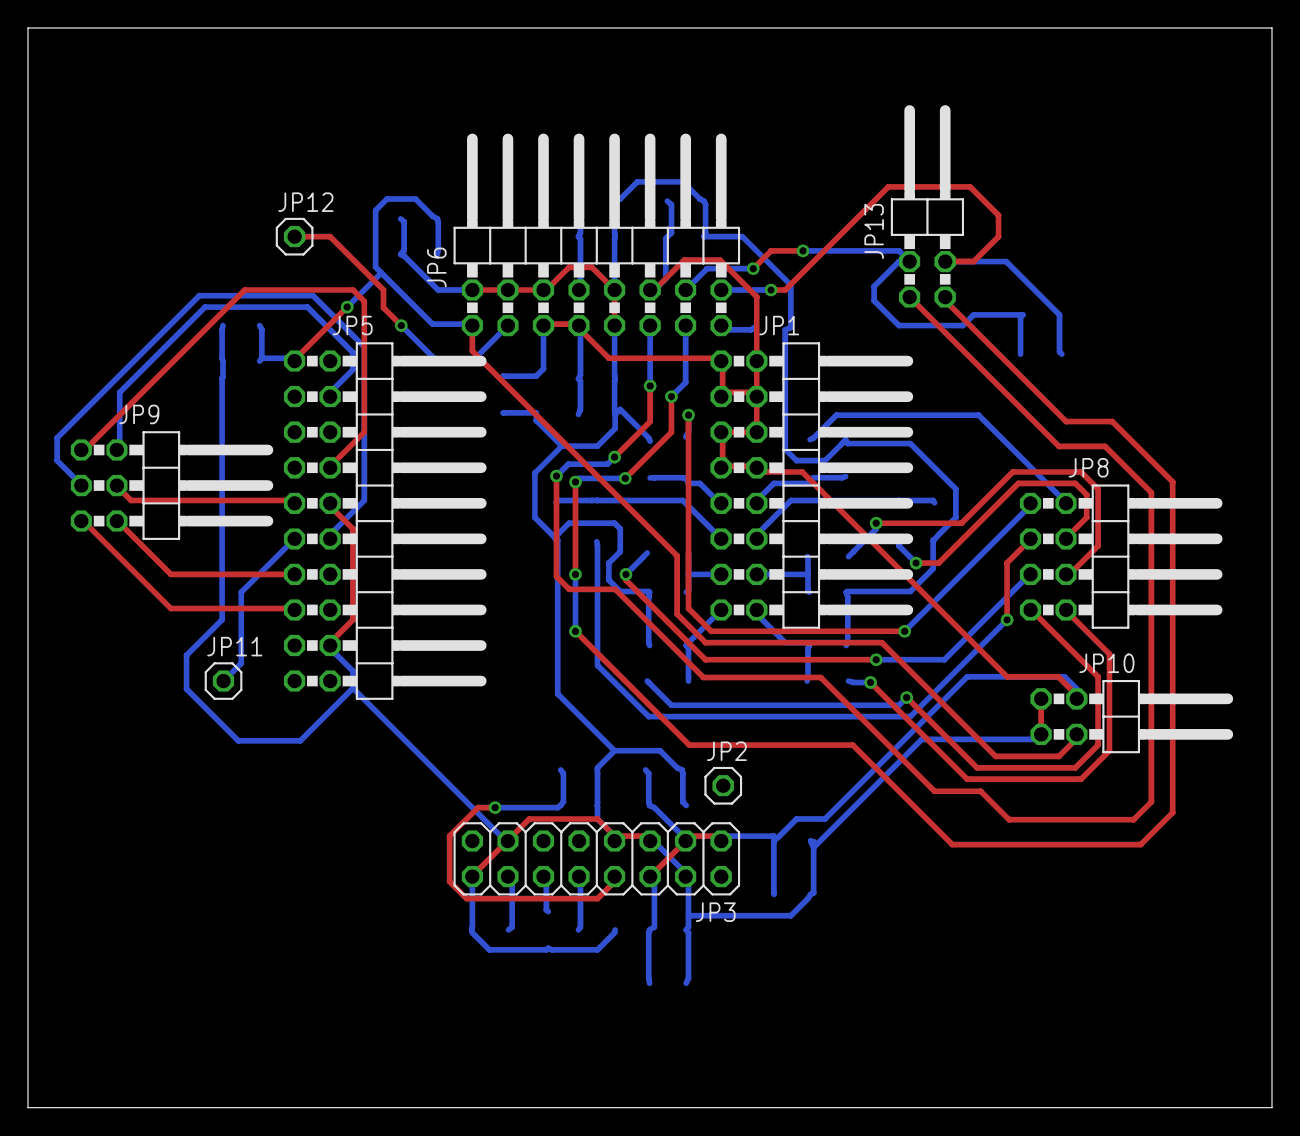
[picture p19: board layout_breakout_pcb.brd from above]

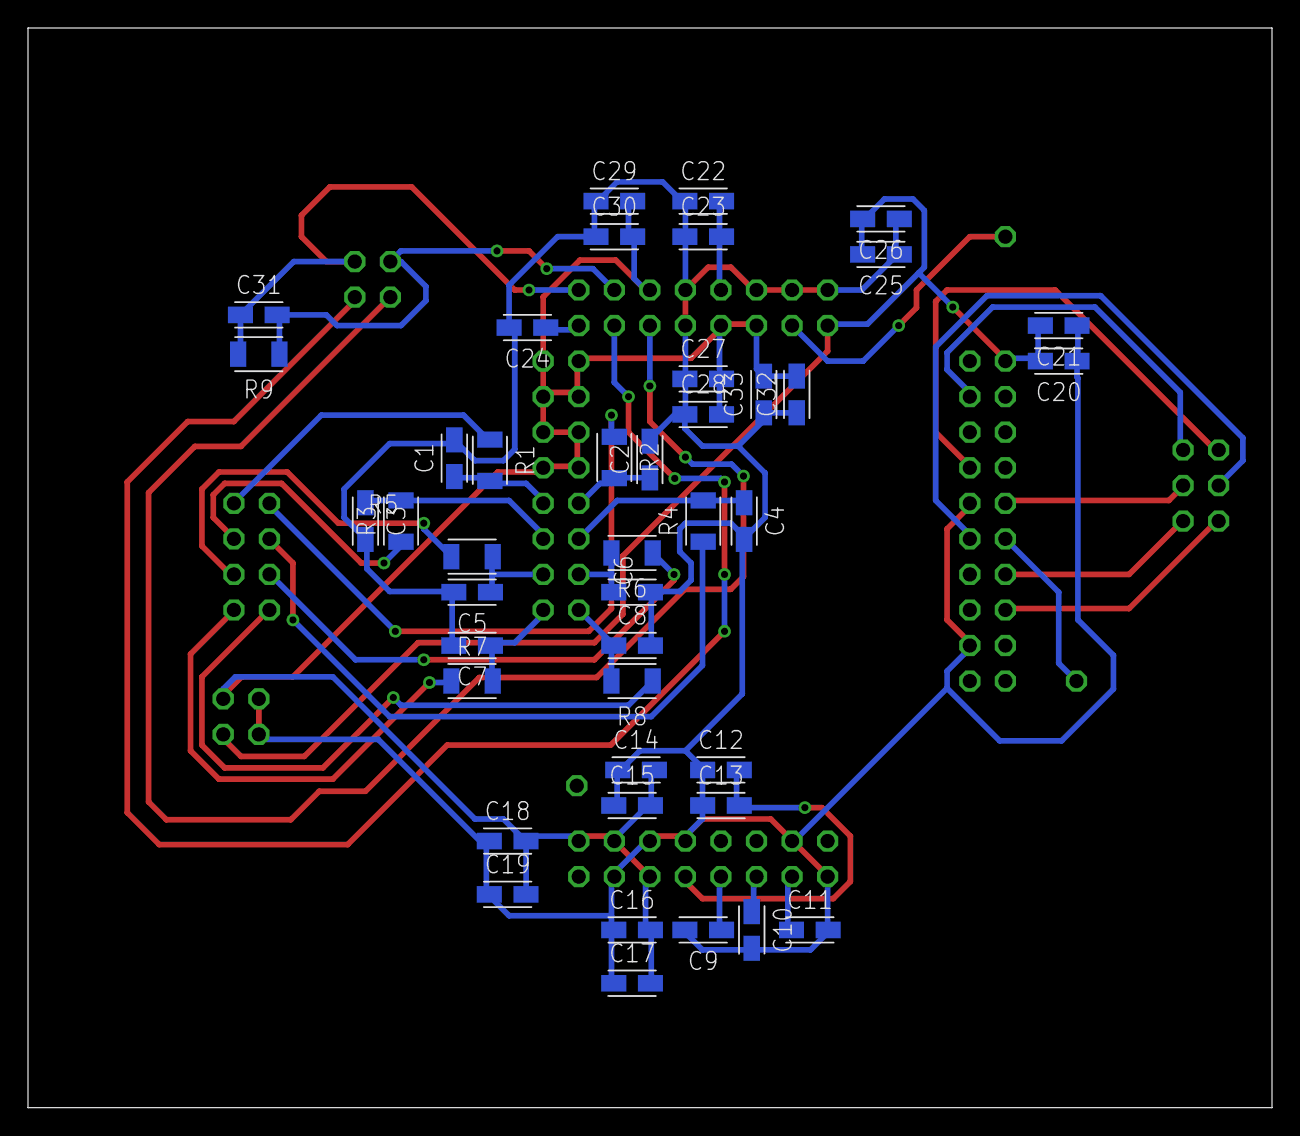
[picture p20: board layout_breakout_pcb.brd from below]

Board: 2 copper layers, 88.9 x 77.1 mm, 53 parts (42 on the bottom side), 37 nets.

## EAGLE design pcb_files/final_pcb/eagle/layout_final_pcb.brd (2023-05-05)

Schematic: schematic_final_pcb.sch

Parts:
C1, C2, C6, C8, C9, C11, C13, C16, C20, C23, C27, C29, C32, C37, C40, C44, C46, C49, C53, C56, C57, C59, C62, C65, C70, C72, C75, C78, C79, C80, C82, C88, C90, C92, C95, C99, C105, C111, C112, C113, C116, C117, C123, C124, C133, C134, C135, C137, C143, C150, C151, C155, C157, C159, C161, C163, C165, C167, C169, C171, C173, C175, C177, C179, C181, C183, C185, C187, C189, C191, C193, C195, C197, C199, C201, C203, C205, C207, C209, C211, C213, C215, C217, C219, C221, C223, C225, C227, C229, C231, C233, C235, C237, C239, C241, C243, C245, C247, C250, C252, C254, C256, C258: 0.1uF; CAPC2012X110
C3, C4, C10, C12, C15, C17, C19, C22, C26, C28, C31, C33, C34, C36, C38, C39, C43, C45, C48, C50, C52, C55, C58, C61, C63, C66, C69, C71, C74, C76, C81, C91, C97, C118, C119, C120, C121, C125, C138, C139, C140, C141, C142, C144, C145, C146, C147, C148, C149, C152, C156, C158, C160, C162, C164, C166, C168, C170, C172, C174, C176, C178, C180, C182, C184, C186, C188, C190, C192, C194, C196, C198, C200, C202, C204, C206, C208, C210, C212, C214, C216, C218, C220, C222, C224, C226, C228, C230, C232, C234, C236, C238, C240, C242, C244, C246, C248, C251, C253, C255, C257, C259: 1uF; CAPC2012X110
C5, C14, C18, C30, C35, C47, C51, C60, C64, C73, C77, C85, C86: 10uF; CAP_293D-A_VSS
C7, C25, C42, C68, C84, C94: 100pF; CAPC1608X85
C21, C87, C89, C96, C100, C132: 2.2uF; CAPC1608X85
C24, C41, C54, C67, C83, C93: 1.5nF; CAPC1608X85
C98: 0.01uF; CAPC2012X110
C101, C102, C122, C136, C153, C154: 22uF; CAPM3216X180
C103, C104, C106, C107, C108, C109, C110, C126, C127, C128, C129, C130, C131: CKCL44X7R1H102M085AACKCL44_TDK-L; CKCL44_TDK-L
C114, C115: 15pF; CAPC1608X85
CR1: BAT85,113DO-34_NEX; DO-34_NEX
FB1, FB2, FB3, FB4, FB5, FB6, FB7, FB8, FB9, FB10, FB11, FB12, FB13, FB14: FERRITE_BEAD; BEADC1608X95N
J1: 3A/250V; B2B-XH-A
JP1, JP5: PINHD-1X6/90; 1X06/90
JP3, JP16, JP18: PINHD-2X3/90; 2X03/90
JP4, JP6: PINHD-1X8/90; 1X08/90
JP7: PINHD-1X7/90; 1X07/90
JP9, JP11, JP13, JP14, JP15, JP17: PINHD-2X4/90; 2X04/90
JP10: PINHD-1X4; 1X04
JP12: PINHD-1X1; 1X01
JP19, JP20, JP21, JP22, JP23, JP24: PINHD-1X2/90; 1X02/90
R1: 1k; RESC1608X60
R2: 470k; RESC1608X60
R3, R4, R5, R6, R7, R8, R10: 1M; RESC1608X60
R9: 10k; RESC1608X60
RN1, RN2, RN3, RN4, RN5, RN6, RN7, RN8, RN9, RN10, RN11, RN12, RN13: CAY16-2201F4LF; RESCAF80P320X160X60-8N
S2: B3U-X000B3U3000P(M)-B3000P(M)-B; B3U-3000P(M)-B
TP1, TP4, TP5, TP7, TP8, TP9, TP10, TP16, TP18, TP19, TP20, TP21, TP22, TP23, TP24, TP25, TP26, TP27, TP28, TP29, TP30: TP; 1X01
TPCS1, TPCS2, TPCS3, TPCS4, TPCS5, TPCS6, TPCS7, TPCS8, TPCS9: TP; 1X01
TPRAW: TP; 1X01
U1, U2, U3, U4, U5, U7: ADS1194CPAG; QFP50P1200X1200X120-64N
U6: LM2664M6; SOT95P280X145-6N
U8: PIC32MX250F128D-I_PT; QFP44_10X10MC
U9: MCP1754T-5002E/MC; SON50P200X300X100-9N
U10: TPS72325QDBVRQ1; SOT95P280X145-5N
U11: TLV70012QDCKRQ1; SOT65P210X110-5N
U13, U14, U15, U16, U17, U18, U19, U20, U21, U22, U23, U24, U25: TPD4E1B06DRLR; SOT50P160X60-6N
U26: LIS3DHHTRQFN_ICLX_STM; QFN_ICLX_STM
XTAL1: 8M; XTALRR488W45L1150T500H350B

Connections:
1N: JP17.7, RN1.3, U13.1 (IO1)
1P: JP17.8, RN1.4, U13.3 (IO2)
2N: JP17.5, RN1.1, U13.4 (IO3)
2P: JP17.6, RN1.2, U13.6 (IO4)
3N: JP17.3, RN2.3, U14.1 (IO1)
3P: JP17.4, RN2.4, U14.3 (IO2)
4N: JP17.1, RN2.1, U14.4 (IO3)
4P: JP17.2, RN2.2, U14.6 (IO4)
5N: JP18.5, RN3.3, U15.1 (IO1)
5P: JP18.6, RN3.4, U15.3 (IO2)
6N: JP18.3, RN3.1, U15.4 (IO3)
6P: JP18.4, RN3.2, U15.6 (IO4)
7N: JP18.1, RN4.3, U16.1 (IO1)
7P: JP18.2, RN4.4, U16.3 (IO2)
8N: JP9.7, RN4.1, U16.4 (IO3)
8P: JP9.8, RN4.2, U16.6 (IO4)
9N: JP15.7, RN5.3, U17.1 (IO1)
9P: JP15.8, RN5.4, U17.3 (IO2)
10N: JP15.5, RN5.1, U17.4 (IO3)
10P: JP15.6, RN5.2, U17.6 (IO4)
11N: JP15.3, RN6.3, U18.1 (IO1)
11P: JP15.4, RN6.4, U18.3 (IO2)
12N: JP15.1, RN6.1, U18.4 (IO3)
12P: JP15.2, RN6.2, U18.6 (IO4)
13N: JP16.5, RN7.3, U19.1 (IO1)
13P: JP16.6, RN7.4, U19.3 (IO2)
14N: JP16.3, RN7.1, U19.4 (IO3)
14P: JP16.4, RN7.2, U19.6 (IO4)
15N: JP16.1, RN8.3, U20.1 (IO1)
15P: JP16.2, RN8.4, U20.3 (IO2)
16N: JP11.7, RN8.1, U20.4 (IO3)
16P: JP11.8, RN8.2, U20.6 (IO4)
17N: JP14.7, RN9.3, U21.1 (IO1)
17P: JP14.8, RN9.4, U21.3 (IO2)
18N: JP14.5, RN9.1, U21.4 (IO3)
18P: JP14.6, RN9.2, U21.6 (IO4)
19N: JP14.3, RN10.3, U22.1 (IO1)
19P: JP14.4, RN10.4, U22.3 (IO2)
20N: JP14.1, RN10.1, U22.4 (IO3)
20P: JP14.2, RN10.2, U22.6 (IO4)
21N: JP3.5, RN11.3, U23.1 (IO1)
21P: JP3.6, RN11.4, U23.3 (IO2)
22N: JP3.3, RN11.1, U23.4 (IO3)
22P: JP3.4, RN11.2, U23.6 (IO4)
23N: JP3.1, RN12.3, U24.1 (IO1)
23P: JP3.2, RN12.4, U24.3 (IO2)
24N: JP13.7, RN12.1, U24.4 (IO3)
24P: JP13.8, RN12.2, U24.6 (IO4)
-RAW: C51.2, C89.1, U6.2 (OUT), U10.1 (IN), U10.2 (EN)
AGND: C1.2, C6.2, C11.2, C12.2, C18.1, C19.2, C20.2, C27.2, C28.2, C35.1, C36.2, C37.2, C38.2, C44.2, C45.2, C51.1, C52.2, C53.2, C57.2, C58.2, C65.2, C66.2, C70.2, C71.2, C78.2, C79.2, C80.2, C87.2, C89.2, C90.2, C95.2, C96.2, C97.2, C98.2, C99.2, C100.2, C103.1, C103.2, C103.3, C103.4, C104.1, C104.2, C104.3, C104.4, C105.2, C106.1, C106.2, C106.3, C106.4, C107.1, C107.2, C107.3, C107.4, C108.1, C108.2, C108.3, C108.4, C109.1, C109.2, C109.3, C109.4, C110.1, C110.2, C110.3, C110.4, C112.1, C116.2, C118.2, C120.2, C123.2, C124.2, C125.2, C126.1, C126.2, C126.3, C126.4, C127.1, C127.2, C127.3, C127.4, C128.1, C128.2, C128.3, C128.4, C129.1, C129.2, C129.3, C129.4, C130.1, C130.2, C130.3, C130.4, C131.1, C131.2, C131.3, C131.4, C131.6, C131.7, C131.8, C132.2, C133.2, C134.2, C135.2, C137.2, C138.2, C139.2, C140.2, C141.2, C142.2, C143.2, C144.2, C145.2, C146.2, C147.2, C148.2, C149.2, C152.2, C155.2, C156.2, C157.2, C158.2, C159.2, C160.2, C161.2, C162.2, C163.2, C164.2, C165.2, C166.2, C169.2, C170.2, C171.2, C172.2, C173.2, C174.2, C175.2, C176.2, C177.2, C178.2, C179.2, C180.2, C181.2, C182.2, C183.2, C184.2, C185.2, C186.2, C187.2, C188.2, C189.2, C190.2, C191.2, C192.2, C193.2, C194.2, C195.2, C196.2, C197.2, C198.2, C199.2, C200.2, C201.2, C202.2, C203.2, C204.2, C205.2, C206.2, C207.2, C208.2, C209.2, C210.2, C211.2, C212.2, C213.2, C214.2, C215.2, C216.2, C217.2, C218.2, C219.2, C220.2, C221.2, C222.2, C223.2, C224.2, C225.2, C226.2, C227.2, C228.2, C229.2, C230.2, C231.2, C232.2, C233.2, C234.2, C235.2, C236.2, C237.2, C238.2, C239.2, C240.2, C241.2, C242.2, C243.2, C244.2, C245.2, C246.2, C247.2, C248.2, FB1.1, FB2.1, FB3.1, FB4.1, FB5.1, FB6.1, FB7.1, FB8.1, FB9.1, FB10.1, FB11.1, FB12.1, FB13.1, FB14.1, J1.2, JP5.4, JP7.3, JP9.3, JP9.4, JP11.3, JP11.4, JP13.3, JP13.4, RN13.2, RN13.3, RN13.4, RN13.5, RN13.6, RN13.7, TP18.1, TP19.1, TP20.1, TP21.1, U6.1 (GND), U8.16 (AVSS), U9.4 (GND), U10.3 (GND), U11.2 (GND), U13.2 (GND), U14.2 (GND), U15.2 (GND), U16.2 (GND), U17.2 (GND), U18.2 (GND), U19.2 (GND), U20.2 (GND), U21.2 (GND), U22.2 (GND), U23.2 (GND), U24.2 (GND), U25.2 (GND), U25.4 (IO3)
AVDD: C1.1, C11.1, C12.1, C18.2, C27.1, C28.1, C44.1, C45.1, C57.1, C58.1, C70.1, C71.1, C100.1, C116.1, C120.1, C133.1, C134.1, C135.1, C137.1, C143.1, C144.1, C145.1, C146.1, C147.1, C148.1, C149.1, C159.1, C160.1, C161.1, C162.1, C163.1, C164.1, C165.1, C166.1, C209.1, C210.1, C211.1, C212.1, C213.1, C214.1, C215.1, C216.1, C217.1, C218.1, C219.1, C220.1, C221.1, C222.1, C223.1, C224.1, C225.1, C226.1, C227.1, C228.1, C229.1, C230.1, C231.1, C232.1, C233.1, C234.1, C235.1, C236.1, C237.1, C238.1, C239.1, C240.1, C241.1, C242.1, C243.1, C244.1, C245.1, C246.1, C247.1, C248.1, JP9.1, JP9.2, JP11.1, JP11.2, JP13.1, JP13.2, TP1.1, U1.1 (IN8N), U1.2 (IN8P), U1.3 (IN7N), U1.4 (IN7P), U1.5 (IN6N), U1.6 (IN6P), U1.7 (IN5N), U1.8 (IN5P), U1.19 (AVDD), U1.21 (AVDD), U1.22 (AVDD), U1.54 (AVDD1), U1.56 (AVDD), U1.59 (AVDD), U2.1 (IN8N), U2.2 (IN8P), U2.3 (IN7N), U2.4 (IN7P), U2.5 (IN6N), U2.6 (IN6P), U2.7 (IN5N), U2.8 (IN5P), U2.19 (AVDD), U2.21 (AVDD), U2.22 (AVDD), U2.54 (AVDD1), U2.56 (AVDD), U2.59 (AVDD), U3.1 (IN8N), U3.2 (IN8P), U3.3 (IN7N), U3.4 (IN7P), U3.5 (IN6N), U3.6 (IN6P), U3.7 (IN5N), U3.8 (IN5P), U3.19 (AVDD), U3.21 (AVDD), U3.22 (AVDD), U3.54 (AVDD1), U3.56 (AVDD), U3.59 (AVDD), U4.1 (IN8N), U4.2 (IN8P), U4.3 (IN7N), U4.4 (IN7P), U4.5 (IN6N), U4.6 (IN6P), U4.7 (IN5N), U4.8 (IN5P), U4.19 (AVDD), U4.21 (AVDD), U4.22 (AVDD), U4.54 (AVDD1), U4.56 (AVDD), U4.59 (AVDD), U5.1 (IN8N), U5.2 (IN8P), U5.3 (IN7N), U5.4 (IN7P), U5.5 (IN6N), U5.6 (IN6P), U5.7 (IN5N), U5.8 (IN5P), U5.19 (AVDD), U5.21 (AVDD), U5.22 (AVDD), U5.54 (AVDD1), U5.56 (AVDD), U5.59 (AVDD), U7.1 (IN8N), U7.2 (IN8P), U7.3 (IN7N), U7.4 (IN7P), U7.5 (IN6N), U7.6 (IN6P), U7.7 (IN5N), U7.8 (IN5P), U7.19 (AVDD), U7.21 (AVDD), U7.22 (AVDD), U7.54 (AVDD1), U7.56 (AVDD), U7.59 (AVDD), U11.5 (OUT), U25.3 (IO2)
AVSS: C2.1, C3.2, C5.2, C6.1, C7.2, C8.2, C10.2, C13.1, C14.2, C15.2, C16.2, C17.2, C19.1, C20.1, C25.2, C26.2, C29.1, C30.2, C31.2, C32.2, C33.2, C34.2, C35.2, C36.1, C37.1, C38.1, C42.2, C43.2, C46.1, C47.2, C48.2, C49.2, C50.2, C52.1, C53.1, C59.1, C60.2, C61.2, C62.2, C63.2, C65.1, C66.1, C68.2, C69.2, C72.1, C73.2, C74.2, C75.2, C76.2, C78.1, C79.1, C80.1, C84.2, C90.1, C94.2, C95.1, C96.1, C97.1, C99.1, C101.2, C102.2, C105.1, C118.1, C119.2, C121.2, C122.2, C123.1, C124.1, C125.1, C136.2, C138.1, C139.1, C140.1, C141.1, C142.1, C152.1, C153.2, C154.2, C155.1, C156.1, C157.1, C158.1, C169.1, C170.1, C171.1, C172.1, C173.1, C174.1, C175.1, C176.1, C177.1, C178.1, C179.1, C180.1, C181.1, C182.1, C183.1, C184.1, C185.1, C186.1, C187.1, C188.1, C189.1, C190.1, C191.1, C192.1, C193.1, C194.1, C195.1, C196.1, C197.1, C198.1, C199.1, C200.1, C201.1, C202.1, C203.1, C204.1, C205.1, C206.1, C207.1, C208.1, TP8.1, U1.20 (AVSS), U1.23 (AVSS), U1.25 (VREFN), U1.32 (AVSS), U1.53 (AVSS1), U1.57 (AVSS), U1.58 (AVSS), U2.20 (AVSS), U2.23 (AVSS), U2.25 (VREFN), U2.32 (AVSS), U2.53 (AVSS1), U2.57 (AVSS), U2.58 (AVSS), U3.20 (AVSS), U3.23 (AVSS), U3.25 (VREFN), U3.32 (AVSS), U3.53 (AVSS1), U3.57 (AVSS), U3.58 (AVSS), U4.20 (AVSS), U4.23 (AVSS), U4.25 (VREFN), U4.32 (AVSS), U4.53 (AVSS1), U4.57 (AVSS), U4.58 (AVSS), U5.20 (AVSS), U5.23 (AVSS), U5.25 (VREFN), U5.32 (AVSS), U5.53 (AVSS1), U5.57 (AVSS), U5.58 (AVSS), U7.20 (AVSS), U7.23 (AVSS), U7.25 (VREFN), U7.32 (AVSS), U7.53 (AVSS1), U7.57 (AVSS), U7.58 (AVSS), U10.4 (OUT), U25.1 (IO1)
BIAS: JP9.5, JP9.6, JP11.5, JP11.6, JP13.5, JP13.6, RN13.1, U25.6 (IO4)
BIAS_ESD: C131.5, RN13.8, U1.60 (RLDREF), U2.60 (RLDREF), U3.60 (RLDREF), U4.60 (RLDREF), U5.60 (RLDREF), U7.60 (RLDREF)
BOOT_EN: R2.2, S2.1, U8.33 (SOSCI/RPB4/RB4)
CLK: JP6.6, JP12.1, U1.37 (CLK), U2.37 (CLK), U3.37 (CLK), U4.37 (CLK), U5.37 (CLK), U7.37 (CLK)
CS1: TPCS1.1, U4.39 (!CS), U8.15 (AN9/C3INA/RPB15/SCK2/CTED6/PMCS1/RB15)
CS2: TPCS2.1, U7.39 (!CS), U8.1 (RPB9/SDA1/CTED4/PMD3/RB9)
CS3: TPCS3.1, U1.39 (!CS), U8.44 (RPB8/SCL1/CTED10/PMD4/RB8)
CS4: TPCS4.1, U2.39 (!CS), U8.43 (RPB7/CTED3/PMD5/INT0/RB7)
CS5: TPCS5.1, U3.39 (!CS), U8.21 (PGED1/AN2/C1IND/C2INB/C3IND/RPB0/PMD0/R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)
CS6: TPCS6.1, U5.39 (!CS), U8.22 (PGEC1/AN3/C1INC/C2INA/RPB1/CTED12/PMD1/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)
CS7: TPCS7.1, U8.34 (SOSCO/RPA4/T1CK/CTED9/RA4), U26.4 (CS)
CS8: JP7.1, TPCS8.1, U8.35 (TDI/RPA9/PMA9/RA9)
CS9: JP6.8, TPCS9.1, U8.38 (RPC5/PMA3/RC5)
DGND: C4.2, C9.2, C21.2, C22.2, C23.2, C39.2, C40.2, C55.2, C56.2, C77.1, C81.2, C82.2, C85.2, C86.1, C88.2, C91.2, C92.2, C111.2, C113.2, C114.2, C115.2, C117.1, C150.2, C151.2, C167.2, C168.2, C250.2, C251.2, C252.2, C253.2, C254.2, C255.2, C256.2, C257.2, C258.2, C259.2, FB1.2, FB2.2, FB3.2, FB4.2, FB5.2, FB6.2, FB7.2, FB8.2, FB9.2, FB10.2, FB11.2, FB12.2, FB13.2, FB14.2, JP4.5, JP6.2, JP7.6, R2.1, TP22.1, TP23.1, TP24.1, TP25.1, TP26.1, TP27.1, TP28.1, TP29.1, U1.31 (RESV1), U1.33 (DGND), U1.41 (DAISY_IN), U1.49 (DGND), U1.51 (DGND), U2.31 (RESV1), U2.33 (DGND), U2.41 (DAISY_IN), U2.49 (DGND), U2.51 (DGND), U3.31 (RESV1), U3.33 (DGND), U3.41 (DAISY_IN), U3.49 (DGND), U3.51 (DGND), U4.31 (RESV1), U4.33 (DGND), U4.41 (DAISY_IN), U4.49 (DGND), U4.51 (DGND), U5.31 (RESV1), U5.33 (DGND), U5.41 (DAISY_IN), U5.49 (DGND), U5.51 (DGND), U7.31 (RESV1), U7.33 (DGND), U7.41 (DAISY_IN), U7.49 (DGND), U7.51 (DGND), U8.6 (VSS_2), U8.29 (VSS_3), U8.39 (VSS), U26.9 (GND_2), U26.10 (GND_3), U26.11 (GND_4), U26.12 (GND_5), U26.13 (GND_6), U26.14 (GND_7), U26.15 (GND_8), U26.16 (GND)
DRDY1: U4.47 (!DRDY), U8.19 (PGED3/VREF+/CVREF+/AN0/C3INC/RPA0/CTED1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)
DRDY2: U7.47 (!DRDY), U8.2 (RPC6/PMA1/RC6)
DRDY3: U1.47 (!DRDY), U8.3 (RPC7/PMA0/RC7)
DRDY4: U2.47 (!DRDY), U8.4 (RPC8/PMA5/RC8)
DRDY5: U3.47 (!DRDY), U8.5 (RPC9/CTED7/PMA6/RC9)
DRDY6: U5.47 (!DRDY), U8.23 (AN4/C1INB/C2IND/RPB2/SDA2/CTED13/PMD2/C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)
DVDD: C4.1, C9.1, C21.1, C22.1, C23.1, C39.1, C40.1, C55.1, C56.1, C77.2, C81.1, C82.1, C86.2, C88.1, C91.1, C92.1, C112.2, C113.1, C117.2, C132.1, C150.1, C151.1, C167.1, C168.1, C250.1, C251.1, C252.1, C253.1, C254.1, C255.1, C256.1, C257.1, C258.1, C259.1, JP4.4, JP6.1, JP7.4, R9.2, S2.2, TP4.1, U1.48 (DVDD), U1.50 (DVDD), U1.52 (CLKSEL), U2.48 (DVDD), U2.50 (DVDD), U2.52 (CLKSEL), U3.48 (DVDD), U3.50 (DVDD), U3.52 (CLKSEL), U4.48 (DVDD), U4.50 (DVDD), U4.52 (CLKSEL), U5.48 (DVDD), U5.50 (DVDD), U5.52 (CLKSEL), U6.4 (!SD), U6.5 (V+), U7.48 (DVDD), U7.50 (DVDD), U7.52 (CLKSEL), U8.10 (VUSB3V3), U8.17 (AVDD), U8.28 (VDD_2), U8.40 (VDD), U9.1 (VOUT), U11.1 (IN), U11.3 (EN), U26.7 (VDDIO), U26.8 (VDD)
EN: JP5.6, U8.26 (AN7/RPC1/RC1)
IN1N: C103.7, RN1.6, U4.15 (IN1N)
IN1P: C103.8, RN1.5, U4.16 (IN1P)
IN2N: C103.5, RN1.8, U4.13 (IN2N)
IN2P: C103.6, RN1.7, U4.14 (IN2P)
IN3N: C104.7, RN2.6, U4.11 (IN3N)
IN3P: C104.8, RN2.5, U4.12 (IN3P)
IN4N: C104.5, RN2.8, U4.9 (IN4N)
IN4P: C104.6, RN2.7, U4.10 (IN4P)
IN5N: C106.7, RN3.6, U7.15 (IN1N)
IN5P: C106.8, RN3.5, U7.16 (IN1P)
IN6N: C106.5, RN3.8, U7.13 (IN2N)
IN6P: C106.6, RN3.7, U7.14 (IN2P)
IN7N: C107.7, RN4.6, U7.11 (IN3N)
IN7P: C107.8, RN4.5, U7.12 (IN3P)
IN8N: C107.5, RN4.8, U7.9 (IN4N)
IN8P: C107.6, RN4.7, U7.10 (IN4P)
IN9N: C108.6, RN5.6, U1.15 (IN1N)
IN9P: C108.5, RN5.5, U1.16 (IN1P)
IN10N: C108.8, RN5.8, U1.13 (IN2N)
IN10P: C108.7, RN5.7, U1.14 (IN2P)
IN11N: C109.6, RN6.6, U1.11 (IN3N)
IN11P: C109.5, RN6.5, U1.12 (IN3P)
IN12N: C109.8, RN6.8, U1.9 (IN4N)
IN12P: C109.7, RN6.7, U1.10 (IN4P)
IN13N: C110.6, RN7.6, U2.15 (IN1N)
IN13P: C110.5, RN7.5, U2.16 (IN1P)
IN14N: C110.8, RN7.8, U2.13 (IN2N)
IN14P: C110.7, RN7.7, U2.14 (IN2P)
IN15N: C126.6, RN8.6, U2.11 (IN3N)
IN15P: C126.5, RN8.5, U2.12 (IN3P)
IN16N: C126.8, RN8.8, U2.9 (IN4N)
IN16P: C126.7, RN8.7, U2.10 (IN4P)
IN17N: C127.6, RN9.6, U3.15 (IN1N)
IN17P: C127.5, RN9.5, U3.16 (IN1P)
IN18N: C127.8, RN9.8, U3.13 (IN2N)
IN18P: C127.7, RN9.7, U3.14 (IN2P)
IN19N: C128.6, RN10.6, U3.11 (IN3N)
IN19P: C128.5, RN10.5, U3.12 (IN3P)
IN20N: C128.8, RN10.8, U3.9 (IN4N)
IN20P: C128.7, RN10.7, U3.10 (IN4P)
IN21N: C129.6, RN11.6, U5.15 (IN1N)
IN21P: C129.5, RN11.5, U5.16 (IN1P)
IN22N: C129.8, RN11.8, U5.13 (IN2N)
IN22P: C129.7, RN11.7, U5.14 (IN2P)
IN23N: C130.6, RN12.6, U5.11 (IN3N)
IN23P: C130.5, RN12.5, U5.12 (IN3P)
IN24N: C130.8, RN12.8, U5.9 (IN4N)
IN24P: C130.7, RN12.7, U5.10 (IN4P)
INT1: U8.41 (RPB5/USBID/RB5), U26.6 (INT1)
MCLR': JP4.1, R1.1, U8.18 (*MCLR)
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

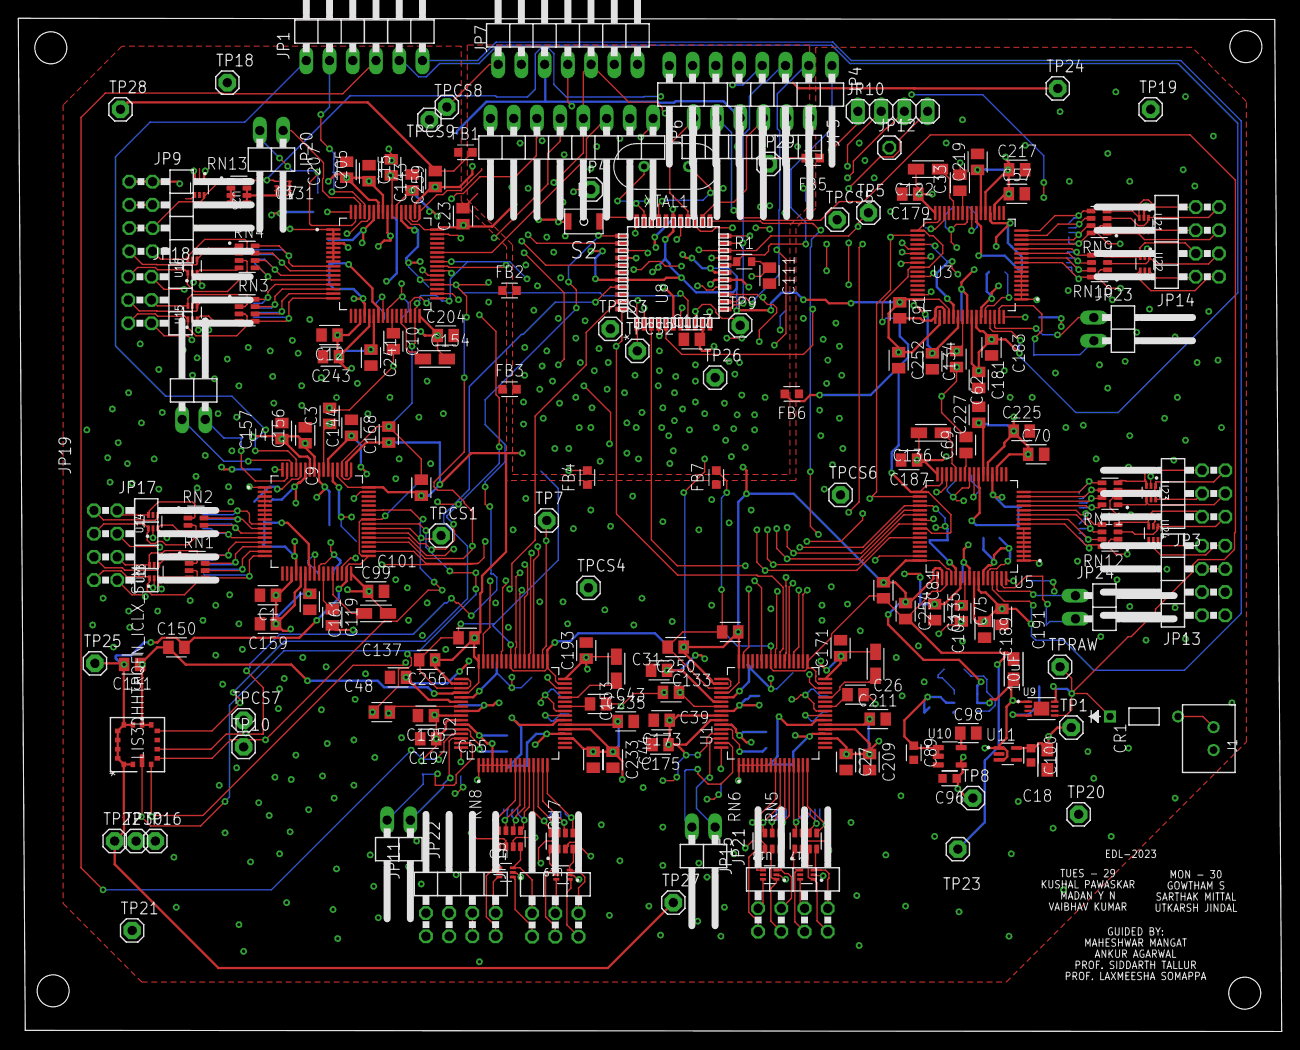
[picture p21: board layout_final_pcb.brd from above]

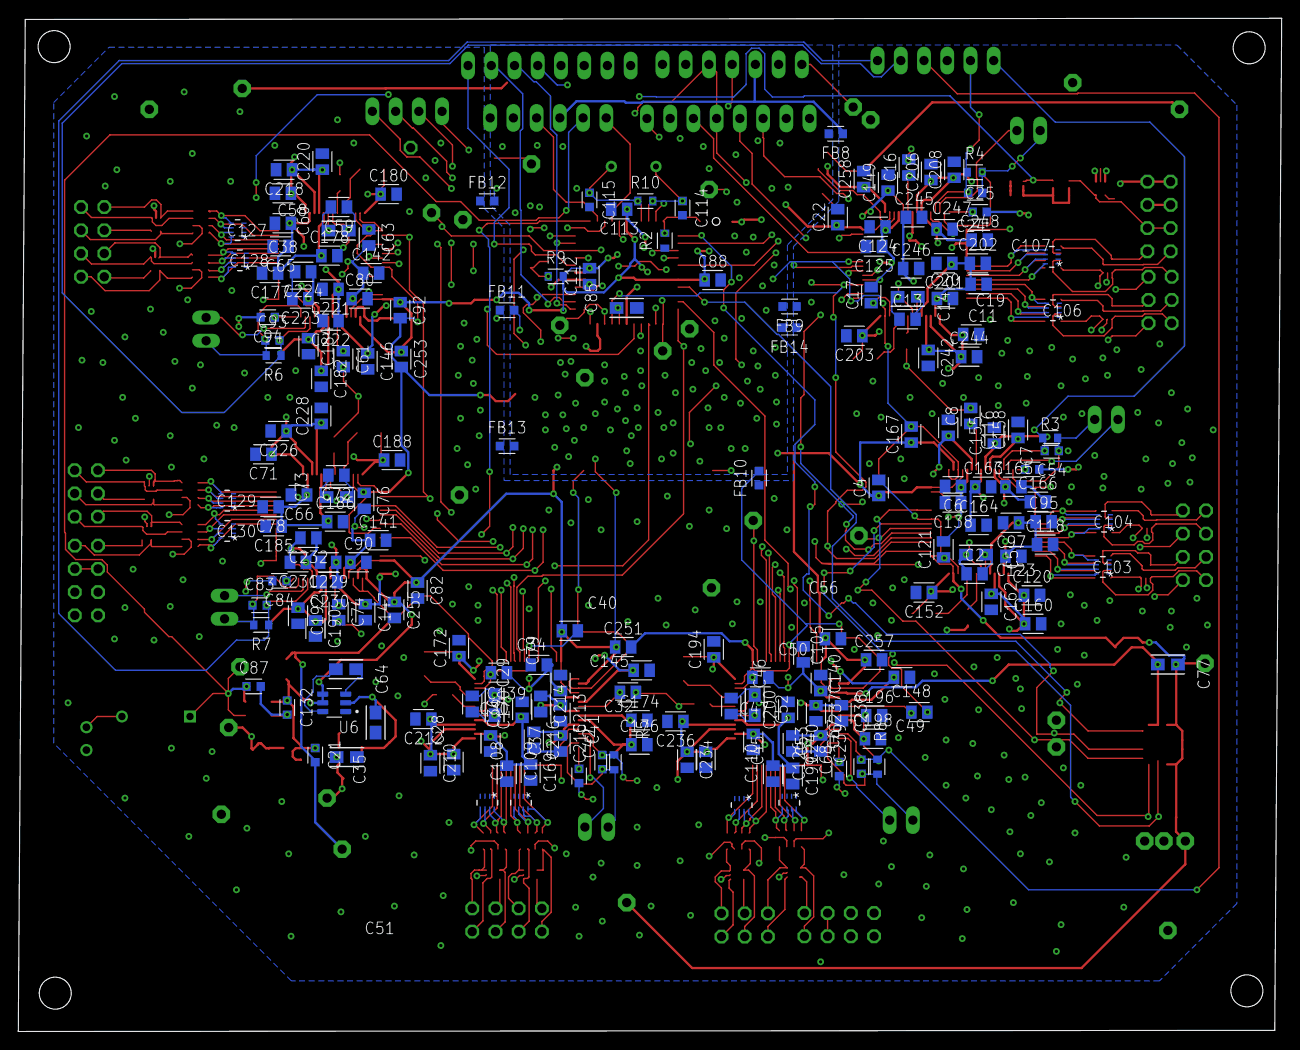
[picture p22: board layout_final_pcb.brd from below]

Board: 4 copper layers, 138.2 x 110.8 mm, 377 parts (192 on the bottom side), 200 nets.

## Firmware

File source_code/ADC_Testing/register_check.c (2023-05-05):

/*	EE344 - Electronic Design Lab
	Groups: TUES-29 and MON-30
	Project: EEG Acquisition System
  
	This code is for initial testing of ADS1194 using PIC32MX clicker board
	IDE used - NECTO Studio v3.0.0
	
	Clock mode: internal

	Supply from clicker board:
	DVDD - 3.3V
	AVDD - 5V "CAUTION: Supply voltages higher than 5.25V can permanently damage the ADC"
	
	SPI Module (clicker):
	CS - pin RG9
	SCLK - pin RG6
	MOSI - pin RG8
	MISO - pin RG7
	RESET - pin RD7
	DRDY(INT) - pin RD11
	
	UART Module (clicker):
	Tx - pin RB14
	Rx - pin RB8
*/


// There are 26 registers
#define no_regs 26

// Defining the pin mappings
sbit cs at RG9_bit;			// chip select' pin
sbit sclk at RG6_bit;		// serial clock pin
sbit dout at RG8_bit;		// uC's data_out, i.e. MOSI pin
sbit din at RG7_bit;		// uC's data_in, i.e. MISO pin
sbit txd at RB14_bit;		// TX pin for UART
sbit rxd at RB8_bit;			// RX pin for UART
sbit reset at RD7_bit;		// RESET' pin
sbit drdy at RD11_bit;		// DRDY' (INT) pin

// Defining the input/output direction variables
sbit cs_direction at TRISG9_bit;
sbit sclk_direction at TRISG6_bit;
sbit dout_direction at TRISG8_bit;
sbit din_direction at TRISG7_bit;
sbit tx_direction at TRISB14_bit;
sbit rx_direction at TRISB8_bit;
sbit reset_direction at TRISD7_bit;
sbit drdy_direction at TRISD11_bit;

// Creating array of registers
char reg[no_regs];


void init(){
	cs_direction = 0;		// set CS' pin as output
	sclk_direction = 0;		// set SCLK pin as output
	dout_direction = 0;		// set MOSI pin as output
	din_direction = 1;		// set MISO pin as input
	tx_direction = 0;		// set TX pin as output
	rx_direction = 1;		// set RX pin as input
	reset_direction = 0;	// set RESET' pin as output
	drdy_direction = 0;		// set DRDY' pin as output

	cs = 1;					// deselect ADC (active low)

	reset = 0;			// reset the ADC (active low)
	Delay_ms(10);		// 10 ms delay
	reset = 1;
	Delay_ms(10);

	SPI2_Init_Advanced(_SPI_MASTER, _SPI_16_BIT, 80, _SPI_SS_DISABLE, _SPI_DATA_SAMPLE_MIDDLE, _SPI_CLK_IDLE_LOW, _SPI_IDLE_2_ACTIVE);		// Initialize SPI Module (Fosc/80 = 1MHz)
	UART5_Init(9600);		// baud rate = 9600
}


int main(){
	
	init();

	cs = 0;				// select ADC (active low)

	SPI2_Write(0x06);	// reset command
	Delay_us(18);		// 18 microsecond delay (18 SCLK cycles required)
	SPI2_Write(0x08);	// start command (to start conversions)
	Delay_us(4);		// 4 SCLK cycles
	SPI2_Write(0x11);	// stop read data continuously mode
	Delay_us(4);		// 4 SCLK cycles		

	Delay_us(8);

	// Set GPIO pins as output
	SPI2_Write(0x4E);	// WREG command 1st opcode byte for GPIO register
	Delay_us(8);		// 8 SCLK cycles
	SPI2_Write(0x00);	// WREG command 2nd opcode byte for GPIO register
	Delay_us(8);
	SPI2_Write(0x00);	// lower nibble sets the 4 GPIO pins as output and upper nibble sets their values to 0

	Delay_us(8);

	UART5_Write_Text("Reading Registers\n");
	SPI2_Write(0x20);			// RREG command 1st opcode byte
	Delay_us(8);				// 8 SCLK cycles required
	SPI2_Write(0x19);			// RREG command 2nd opcode byte
	Delay_us(8);

	int i = 0;
	while(i<26){
		reg[i] = SPI2_Read(0);	// reading register data
		Delay_us(8);			// 8 SCLK cycles
		i++;
	}

	i = 0;
	while(i<26){
		char temp1 = reg[i] & 0x0F;		// separating the nibbles to see data in hex format (lower nibble here)
		char temp2 = reg[i] >> 4;		// upper nibble
		UART5_Write(temp2 + 48);		// ASCII value of 0 is 48
		UART5_Write(temp1 + 48);
		UART5_Write_Text("\n");
		i++;
	}

	while(1){

	}
	
	return 0;
}

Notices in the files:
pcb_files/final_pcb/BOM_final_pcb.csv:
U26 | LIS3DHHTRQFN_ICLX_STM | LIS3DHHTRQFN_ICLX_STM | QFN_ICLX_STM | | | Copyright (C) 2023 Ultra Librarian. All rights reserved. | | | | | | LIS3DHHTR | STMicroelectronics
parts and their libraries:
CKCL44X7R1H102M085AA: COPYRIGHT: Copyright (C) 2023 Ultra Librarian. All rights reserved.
